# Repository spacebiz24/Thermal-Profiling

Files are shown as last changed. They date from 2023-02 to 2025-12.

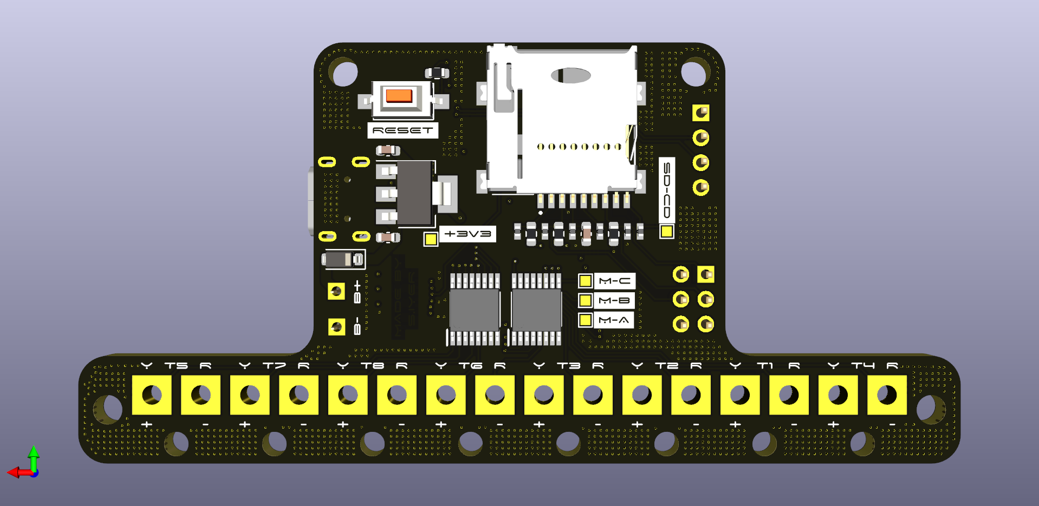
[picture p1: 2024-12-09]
Hardware/Plots/Temperature Thing With Thermocouple 3V3 Bottom.png

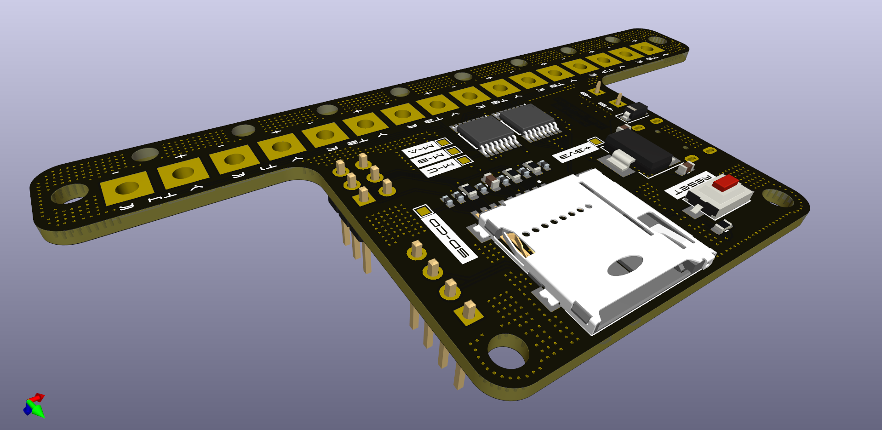
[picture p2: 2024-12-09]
Hardware/Plots/Temperature Thing With Thermocouple 3V3 Bottom Perspective.png

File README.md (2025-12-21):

# Thermal Profiling on Fabrics

This repository is divided into the following sections:

```mermaid
graph TD;
Repo --> Dashboard
Repo --> Documentation
Repo --> Firmware
Repo --> Hardware
Repo --> Thermoscope
```

Each section explains more about itself in its own `README.md` file. Please look into them.
___
Made with :heart: by [spacebiz24](https://github.com/spacebiz24), [dkoppad3](https://github.com/dkoppad3), [DivakarGC](https://github.com/DivakarGC), [naruto4526](https://github.com/naruto4526), [Eloquencere](https://github.com/Eloquencere), [Tejas-M-Nayak](https://github.com/Tejas-M-Nayak) and [L-o-n-e-W-o-l-f](https://github.com/L-o-n-e-W-o-l-f)

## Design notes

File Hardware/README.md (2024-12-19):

# Hardware
This directory contains all the files concerning the project hardware, including the PCB and the overall casing.

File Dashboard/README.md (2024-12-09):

# Dashboard
This directory contains all the files that were used to build the dashboard to display data.
Two versions were built, one implemented on a PC and the other implemented on a Raspberry Pi GUI unit.
More information can be found by looking into the sub-directories.
___
> [!WARNING]
> This version is deprecated. The final version used is found in `/Thermoscope`.

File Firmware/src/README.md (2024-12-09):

# Temperature Thing Firmware
<p align="center">
    <i align="center">The firmware running the temperature sensing platform built for DRDO. 🌡️ </i>
</p>
<p align="center">
    
    
    <br>
    
    
</p>

___

## Contents
1. [Architecture of the Firmware](#architecture-of-the-firmware)
1. [Some important pointers about the firmware](#some-important-pointers-about-the-firmware)
1. [Functions in the Firmware](#functions-in-the-firmware)
1. [Continuous Integration Pipeline](#continuous-integration-pipeline)
1. [Authors and Reviewers](#authors-and-reviewers)
1. [License](#license)

## Architecture of the Firmware
This firmware was written to interface the ATMega328P with MAX31856 ADC.
All the underlying code is written in C++ and is built using the PlatformIO framework.
The main code loop heavily relies upon the custom built MAX31856 library which is 
covered in detail in the
[library documentation](https://github.com/spacebiz24/Thermal-Profiling/tree/main/Firmware/lib/MAX31856/).

The actions performed by this firmware are:
- Choose a specific thermocouple using the MUX
- Read the temperature from the MAX31856
- Write the temperature to the serial port and SD card in CSV format
- Repeat the process all over again

The following flow chart describes the overall working of the firmware.
```mermaid
graph TD;
A[Initialise the ATMega328P Pins] --> B[Remove the existing 'data.txt' file from the SD card];
B --> C[Disable the SD card];
C --> D[Enable the MAX31856];
D --> E[Cycle through all the thermocouples and store data];
E --> F[Disable the MAX31856];
F --> G[Enable the SD card];
G --> H[Write the data to the SD card];
H --> C;
```

## Some important pointers about the firmware
All board pins are defined in the beginning of the firmware and must not be changed
as long as hardware does not change. The `SWITCHING_DELAY_MS` defines the delay between
every thermocouple and is set to ensure appropriate time for the ADC readings to be stored
without any mix up.

### Functions in the Firmware
- `selectPin(int Pin_Number)`
    - This function is used to select a specific pin using the MUX.
    - Parameters:
        - `Pin_Number`: The pin number to be selected on the MUX.
    - Returns:
        - None
- `readSingleThermocouple(int Thermocouple_Number)`
    - This function is used to read the temperature from a single thermocouple.
    It selects a thermocouple by invoking the `selectPin()` function and then reads
    the temperature from the MAX31856.
    - Parameters:
        - None
    - Returns:
        - None
- `cycleThroughThermocouples()`
    - This function is used to cycle through all the thermocouples and store the data.
    - Parameters:
        - None
    - Returns:
        - None

The `setup()` function in the firmware initialises all the pins and their directions by using the
`BOARD_PINS` and `MUX_PINS` arrays which are defined in the beginning of the firmware.
The `BOARD_PINS_DIR` array defines the direction of the pins in the `BOARD_PINS` array.
The same is not needed for `MUX_PINS` as all the pins are set as `OUTPUT`.

The `setup()` function also removes the existing data file from the SD card to ensure that new data
is always written every time. It also initialises serial communication.

The `loop()` function follows all the steps as described in the flow chart above and calls the
`cycleThroughThermocouples()` function to cycle through all the thermocouples before writing
the same data to the SD card along with the time stamp to allow easier logging.

## Continuous Integration Pipeline
The firmware is built using the PlatformIO framework and is tested using the GitHub Actions CI pipeline.
The pipeline is triggered on every push to the repository and runs the firmware on a virtual environment
and the same is configured using the `.github/workflows/main.yml` file.

## Authors
<p align="center">
<center>
<div style="display: flex; justify-content: center;" align="center">
<figure>
    <a href="https://github.com/spacebiz24">
        spacebiz24
    </a>
</figure>
</div>
</center>
</p>

## Reviewers
<p align="center">
<center>
<div style="display: flex; justify-content: center;" align="center">
<figure>
    <a href="https://github.com/Eloquencere">
        Eloquencere
    </a>
</figure>
<figure>
    <a href="https://github.com/Tejas-M-Nayak">
        Tejas-M-Nayak
    </a>
</figure>
</div>
</center>
</p>

## License
As most of the project except the SD card library is custom developed,
without prior written permission of the author, this code must not be
reproduced, displayed, modified or distributed. The SD card library is
not covered under the above license. For more information, please refer
to the LICENSE file in the root directory of the repository.

___

Made with :heart: by [spacebiz24](https://github.com/spacebiz24)

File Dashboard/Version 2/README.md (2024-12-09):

# Version 2 of the Dashboard

> [!WARNING]
> This version is deprecated. The final version used is found in `/Thermoscope`.

## SDA Troubleshooting Device

Sensor Data Analysis and Troubleshooting Device

## GUI component for troubleshooting purposes 

- Automatically mounts any drive (storage - USB, MMC)
- Copies data from the mounted drive and reboots
- Automatically runs the GUI on startup

## Setup:

1. Edit autorun to run UIV20.py on startup
2. Edit rc.local to run copy_meow.py in background
3. Reboot pi and have fun :)

### Note: Please do clone the repository and then install the dependencies.

```
git clone https://github.com/spacebiz24/Thermal-Profiling.git

pip install -r requirements.txt
```
___
Made with :heart: by [DivakarGC](https://github.com/DivakarGC)

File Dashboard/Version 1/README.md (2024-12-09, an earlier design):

# Version 1 of the Dashboard
This is version 1 of the dashboard, implemented on a PC that reads files from an SD card and displays data.

> [!WARNING]
> This version is deprecated. The final version used is found in `/Thermoscope`.

___
## Helpful Links

### Tkinter
[Use a Drag & Drop Editor to Make Tkinter Python GUI Applications!](https://www.youtube.com/watch?v=oLxFqpUbaAE)

[TkinterDesigner Documentation](https://github.com/ParthJadhav/Tkinter-Designer/blob/master/docs/instructions.md)

[Make Modern Python Dashboards With Tkinter & Matplotlib!](https://www.youtube.com/watch?v=0H19QzbBqC4)

[How to create multiple Screens/Frames using tkinter python. Tkinter Multiple Frames](https://www.youtube.com/watch?v=3yeRcxkth0I)

[Tkinter Application to Switch Between Different Page Frames](https://www.geeksforgeeks.org/tkinter-application-to-switch-between-different-page-frames/)

[How To Animate Widgets - Python Tkinter GUI Tutorial](https://www.youtube.com/watch?v=kvd6i1mXec8)

#### Tkinter Add-ons

[The ultimate introduction to modern GUIs in Python w/ tkinter](https://www.youtube.com/watch?v=mop6g-c5HEY)

[Make Tkinter Look 10x Better in 5 Minutes (CustomTkinter)](https://www.youtube.com/watch?v=Miydkti_QVE)

[CustomTkinter](https://github.com/TomSchimansky/CustomTkinter)

[tksheet](https://github.com/ragardner/tksheet)

[Python Tkinter GUI Design Using ttkbootstrap - Complete Course](https://www.youtube.com/watch?v=0tM-l_ZsxjU)

[ttkbootstrap](https://ttkbootstrap.readthedocs.io/en/latest/)

### GUI on Startup
[Convert GUI App to Real Program - Python to exe to setup wizard](https://www.youtube.com/watch?v=p3tSLatmGvU)

[The 8 Best Lightweight Operating Systems for Raspberry Pi](https://www.makeuseof.com/tag/lightweight-operating-systems-raspberry-pi/)

[Simple OS to run Tkinter Program](https://forums.raspberrypi.com/viewtopic.php?t=284516)

[Launch a GUI Tkinter program on boot](https://raspberrypi.stackexchange.com/questions/98944/launch-a-gui-tkinter-program-on-boot)

[How to get Python tkinter application to run automatically](https://stackoverflow.com/questions/76020133/how-to-get-python-tkinter-application-to-run-automatically-and-reliably-at-rpi)

___
Made with :heart: by [Eloquencere](https://github.com/Eloquencere) and [L-o-n-e-W-o-l-f](https://github.com/L-o-n-e-W-o-l-f)

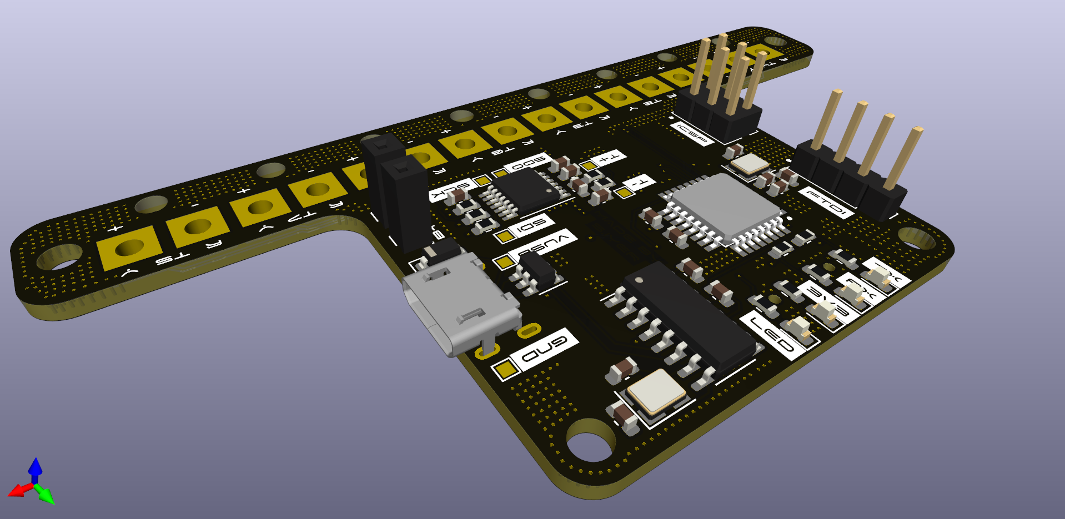
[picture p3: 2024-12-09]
Hardware/Plots/Temperature Thing With Thermocouple 3V3 Top Perspective.png

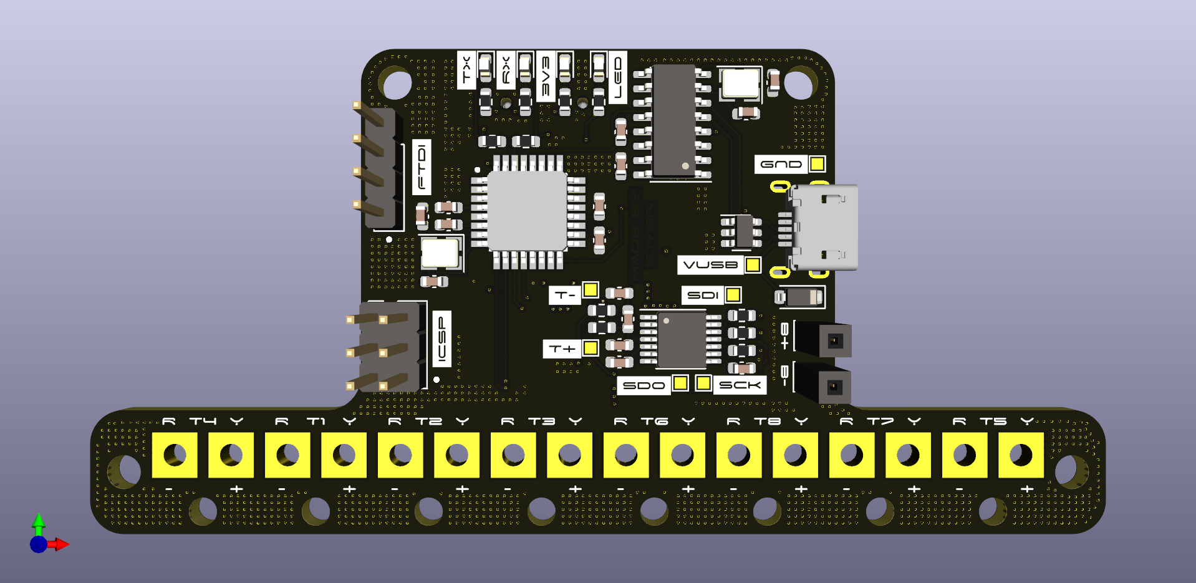
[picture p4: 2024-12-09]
Hardware/Plots/Temperature Thing With Thermocouple 3V3 Top.png

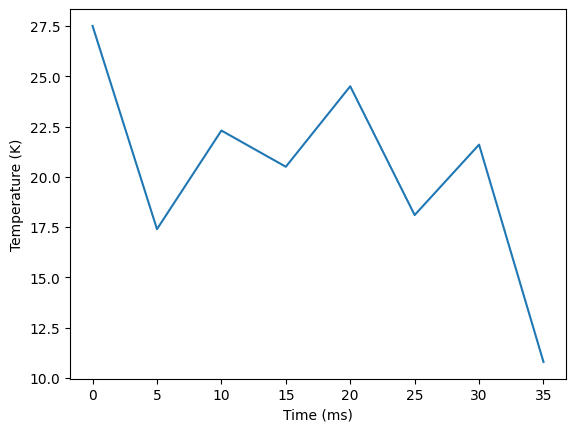
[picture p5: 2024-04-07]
Dashboard/Version 2/assets/Images/fig1.png

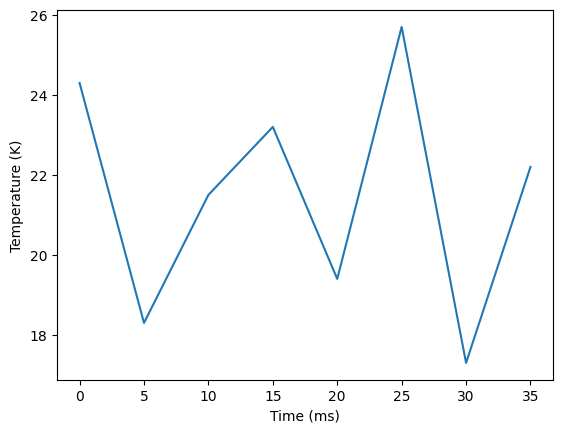
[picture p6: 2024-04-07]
Dashboard/Version 2/assets/Images/fig6.png

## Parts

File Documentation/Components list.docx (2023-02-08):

Sensors

Name | | Temperature Range | Accuracy
Thermocouple | K-Type – RdF Corporations | -184°C to +700°C | 2.2°C or 0.75%
| T-Type – Thermo Sensors | -50° to 200°C | 0.5°C or 0.75%
RTD Temperature sensor | HoneyWell | -55 °C to 150°C | ±0.5°C or ±0.2%
| Auxitrol Weston | -55°C to +322°C | ± 0.50°C
Thermistor | Semitec - 502NT-4-R025H395 | -50°C to 300°C | 1%
| Amphenol - DC95G503VN | -80°C to 150°C | ±0.1°C

Microcontroller

Name | Temperature range | Operating Voltage | ADC
Freescale Semiconductor - MPC5554 – 32-bit | –40° C to 125° C | 1.5 V ± 10% | 12-bit
Maxim Integrated MAXQ7670A – 16-bit | -40°C to +125°C | 2.5V | 12-bit
Vorago Technologies VA41620 – 32-bit | -55 to 125℃ | 3.3 +/- 0.33V | 12-bit
Atmel SAM3X8E – 32-bit | -55°C to 105°C | 1.62V | 12-bit
Microchip ATmegaS64M1 – 8-bit | -55 °C to +125 °C | 3.3V | 10-bit

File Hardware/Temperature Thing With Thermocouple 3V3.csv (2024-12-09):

Source: | C:\Users\Desktop\Documents\KiCad\Temperature Thing With Thermocouple 3V3\Temperature Thing With Thermocouple 3V3.kicad_sch
Date: | 08-07-2024 10:46:44
Tool: | Eeschema (7.0.0)
Generator: | C:\Program Files\KiCad\7.0\bin\scripting\plugins/bom_csv_grouped_by_value.py
Component Count: | 86
Collated Components:
Item | Qty | Reference(s) | Value | LibPart | Footprint | Datasheet | DNP | Height | MANUFACTURER | Manufacturer_Name | Manufacturer_Part_Number | Mouser Part Number | Mouser Price/Stock | Sim.Device | Sim.Pins
1 | 6 | C1, C2, C3, C5, C7, C13 | 100n | Device:C | Capacitor_SMD:C_0603_1608Metric | ~
2 | 2 | C4, C8 | 10n | Device:C | Capacitor_SMD:C_0603_1608Metric | ~
3 | 4 | C6, C9, C15, C16 | 22p | Device:C | Capacitor_SMD:C_0603_1608Metric | ~
4 | 2 | C10, C12 | 1u | Device:C | Capacitor_SMD:C_0603_1608Metric | ~
5 | 1 | C11 | 4.7u | Device:C | Capacitor_SMD:C_0603_1608Metric | ~
6 | 1 | C14 | 10u | Device:C | Capacitor_SMD:C_0603_1608Metric | ~
7 | 2 | C17, C18 | 10u | Device:C_Polarized_US | Capacitor_SMD:C_0603_1608Metric | ~
8 | 4 | D1, D2, D3, D4 | LED | Device:LED | LED_SMD:LED_0603_1608Metric | ~
9 | 2 | D5, D6 | 1N4148 | Diode:1N4148 | Diode_SMD:D_SOD-123 | https://assets.nexperia.com/documents/data-sheet/1N4148_1N4448.pdf |  |  |  |  |  |  |  |  | D | 1=K 2=A
10 | 1 | J1 | T1+ | Connector:Conn_01x01_Pin | Connector_PinHeader_1.27mm:PinHeader_1x01_P1.27mm_Vertical | ~
11 | 1 | J2 | T2+ | Connector:Conn_01x01_Pin | Connector_PinHeader_1.27mm:PinHeader_1x01_P1.27mm_Vertical | ~
12 | 1 | J3 | T3+ | Connector:Conn_01x01_Pin | Connector_PinHeader_1.27mm:PinHeader_1x01_P1.27mm_Vertical | ~
13 | 1 | J4 | T4+ | Connector:Conn_01x01_Pin | Connector_PinHeader_1.27mm:PinHeader_1x01_P1.27mm_Vertical | ~
14 | 1 | J5 | T5+ | Connector:Conn_01x01_Pin | Connector_PinHeader_1.27mm:PinHeader_1x01_P1.27mm_Vertical | ~
15 | 1 | J6 | T6+ | Connector:Conn_01x01_Pin | Connector_PinHeader_1.27mm:PinHeader_1x01_P1.27mm_Vertical | ~
16 | 1 | J7 | T7+ | Connector:Conn_01x01_Pin | Connector_PinHeader_1.27mm:PinHeader_1x01_P1.27mm_Vertical | ~
17 | 1 | J8 | T8+ | Connector:Conn_01x01_Pin | Connector_PinHeader_1.27mm:PinHeader_1x01_P1.27mm_Vertical | ~
18 | 1 | J9 | T1- | Connector:Conn_01x01_Pin | Connector_PinHeader_1.27mm:PinHeader_1x01_P1.27mm_Vertical | ~
19 | 1 | J10 | T2- | Connector:Conn_01x01_Pin | Connector_PinHeader_1.27mm:PinHeader_1x01_P1.27mm_Vertical | ~
20 | 1 | J11 | T3- | Connector:Conn_01x01_Pin | Connector_PinHeader_1.27mm:PinHeader_1x01_P1.27mm_Vertical | ~
21 | 1 | J12 | T4- | Connector:Conn_01x01_Pin | Connector_PinHeader_1.27mm:PinHeader_1x01_P1.27mm_Vertical | ~
22 | 1 | J13 | USB_B_Micro | Connector:USB_B_Micro | Connector_USB:USB_Micro-B_Molex_47346-0001 | ~
23 | 1 | J14 | T5- | Connector:Conn_01x01_Pin | Connector_PinHeader_1.27mm:PinHeader_1x01_P1.27mm_Vertical | ~
24 | 1 | J15 | T6- | Connector:Conn_01x01_Pin | Connector_PinHeader_1.27mm:PinHeader_1x01_P1.27mm_Vertical | ~
25 | 1 | J16 | B+ | Connector:Conn_01x01_Pin | Connector_PinSocket_2.54mm:PinSocket_1x01_P2.54mm_Vertical | ~
26 | 1 | J17 | T7- | Connector:Conn_01x01_Pin | Connector_PinHeader_1.27mm:PinHeader_1x01_P1.27mm_Vertical | ~
27 | 1 | J18 | ICSP | Connector_Generic:Conn_02x03_Odd_Even | Connector_PinHeader_2.54mm:PinHeader_2x03_P2.54mm_Vertical | ~
28 | 1 | J19 | T8- | Connector:Conn_01x01_Pin | Connector_PinHeader_1.27mm:PinHeader_1x01_P1.27mm_Vertical | ~
29 | 1 | J20 | B- | Connector:Conn_01x01_Pin | Connector_PinSocket_2.54mm:PinSocket_1x01_P2.54mm_Vertical | ~
30 | 7 | R1, R2, R3, R6, R7, R14, R15 | 1k | Device:R_US | Resistor_SMD:R_0603_1608Metric | ~
31 | 2 | R4, R5 | 100 | Device:R_US | Resistor_SMD:R_0603_1608Metric | ~
32 | 6 | R8, R9, R10, R11, R12, R13 | 10k | Device:R_US | Resistor_SMD:R_0603_1608Metric | ~
33 | 6 | RV1, RV2, RV3, RV4, RV5, RV6 | CG0402MLU-3.3G | CG402MLU-3_3G:CG0402MLU-3.3G | CG402MLU-3_3G:CG402MLU-3_3G | https://www.bourns.com/docs/Product-Datasheets/MLU.pdf |  |  | 0.41 |  | Bourns | CG0402MLU-3.3G | 652-CG0402MLU-3.3G | https://www.mouser.co.uk/ProductDetail/Bourns/CG0402MLU-3.3G?qs=m8myXnDJXpWVM8EQWErxtQ%3D%3D
34 | 1 | SW1 | SW_Push | Switch:SW_Push | Button_Switch_SMD:SW_SPST_CK_RS282G05A3 | ~
35 | 10 | TP1, TP2, TP3, TP4, TP5, TP6, TP7, TP8, TP9, TP10 | ~ | Connector:TestPoint | TestPoint:TestPoint_Pad_1.0x1.0mm | ~
36 | 1 | U1 | CH340G | Interface_USB:CH340G | Package_SO:SOIC-16_3.9x9.9mm_P1.27mm | http://www.datasheet5.com/pdf-local-2195953
37 | 1 | U2 | MAX31856 | Sensor_Temperature:MAX31856 | Package_SO:TSSOP-14_4.4x5mm_P0.65mm | https://datasheets.maximintegrated.com/en/ds/MAX31856.pdf
38 | 2 | U3, U6 | CD4051B | Analog_Switch:CD4051B | CD4051BPWR:CD4051BPWR | http://www.ti.com/lit/ds/symlink/cd4052b.pdf
39 | 1 | U4 | microSD Card | GCT-MICROSD-HOLDER:GCT-MICROSD-HOLDER | GCT-MICROSD-HOLDER:GCT-MICROSD-HOLDER
40 | 1 | U5 | ATMEGA328P-AU | ATMEGA328P-AU:ATMEGA328P-AU | ATMEGA328P-AU:ATMEGA328P-AU |  |  |  |  | Atmel
41 | 1 | U7 | USBLC6-2SC6 | Power_Protection:USBLC6-2SC6 | Package_TO_SOT_SMD:SOT-23-6 | https://www.st.com/resource/en/datasheet/usblc6-2.pdf
42 | 1 | U8 | AMS1117-3.3 | Regulator_Linear:AMS1117-3.3 | Package_TO_SOT_SMD:SOT-223-3_TabPin2 | http://www.advanced-monolithic.com/pdf/ds1117.pdf
43 | 1 | Y1 | 12MHz | Device:Crystal_GND24 | Crystal:Crystal_SMD_3225-4Pin_3.2x2.5mm | ~
44 | 1 | Y2 | 16MHz | Device:Crystal_GND24 | Crystal:Crystal_SMD_3225-4Pin_3.2x2.5mm | ~

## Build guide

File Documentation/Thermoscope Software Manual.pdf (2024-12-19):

# T H E R M O S C O P E S O F T W A R E M A N U A L

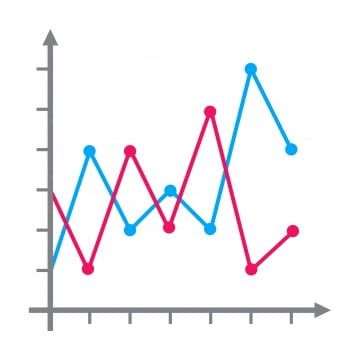
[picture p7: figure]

# A B O U T T H E A P P

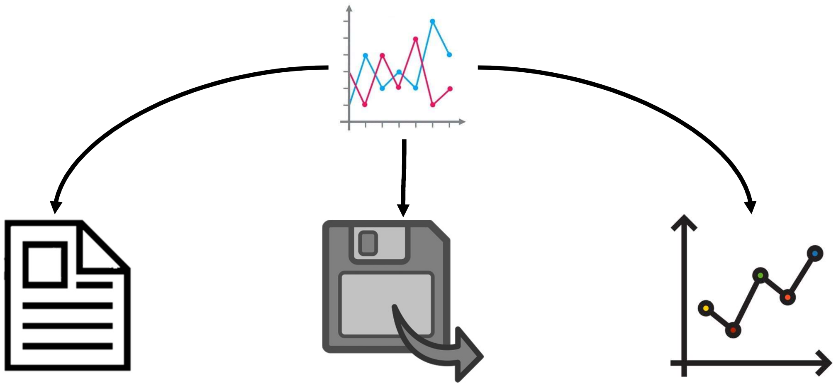
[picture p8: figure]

Read | Capture | Visualise

# I M P O R T A N T !

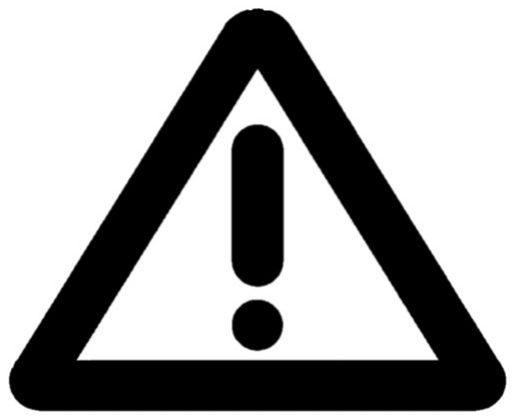
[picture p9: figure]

# Please follow the steps in the specified order for reliable

performance.

# S T E P 1 : C O N N E C T I N G T H E S D C A R D

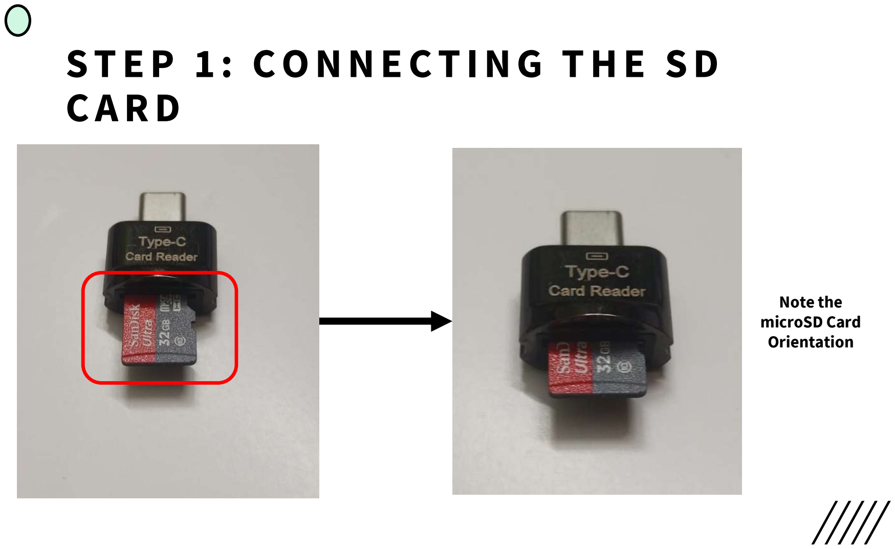
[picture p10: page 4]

Note the
microSD Card
Orientation

# S T E P 2 : C O N N E C T I N G T H E S D C A R D R E A D E R

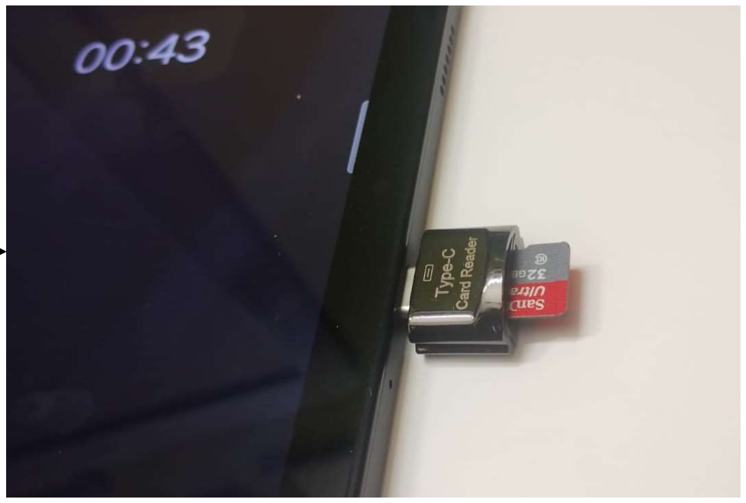
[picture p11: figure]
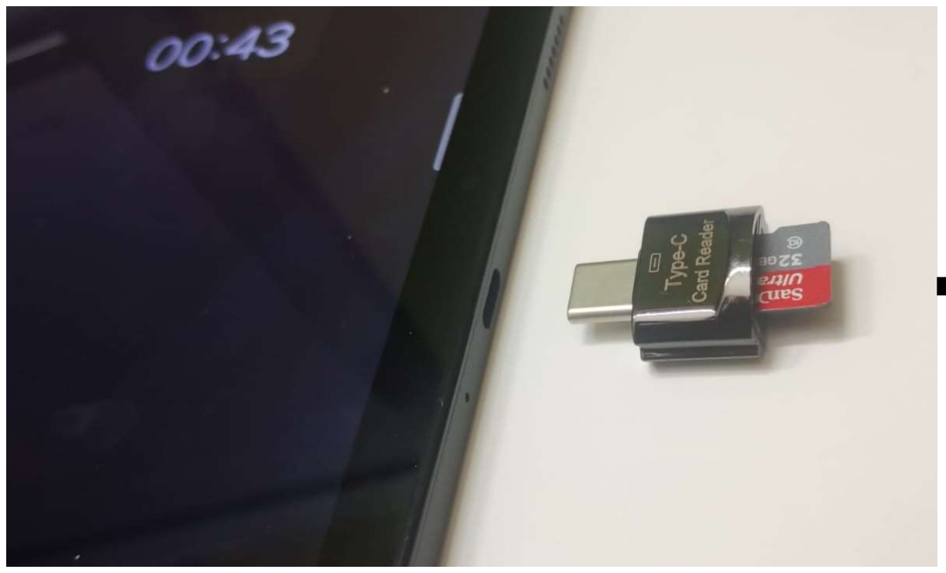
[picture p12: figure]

# S T E P 3 : O P E N I N G T H E A P P

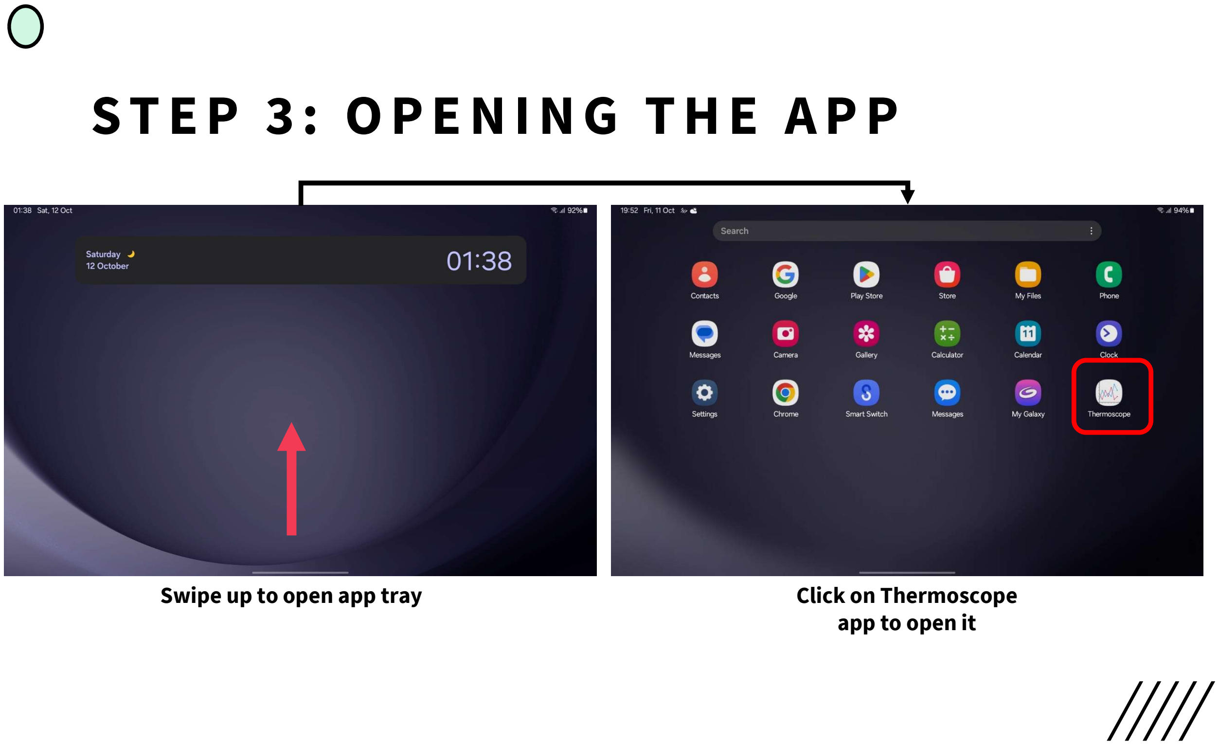
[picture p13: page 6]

Swipe up to open app tray | Click on Thermoscope app to open it

# S T E P 4 : S A V I N G T H E D A T A F I L E

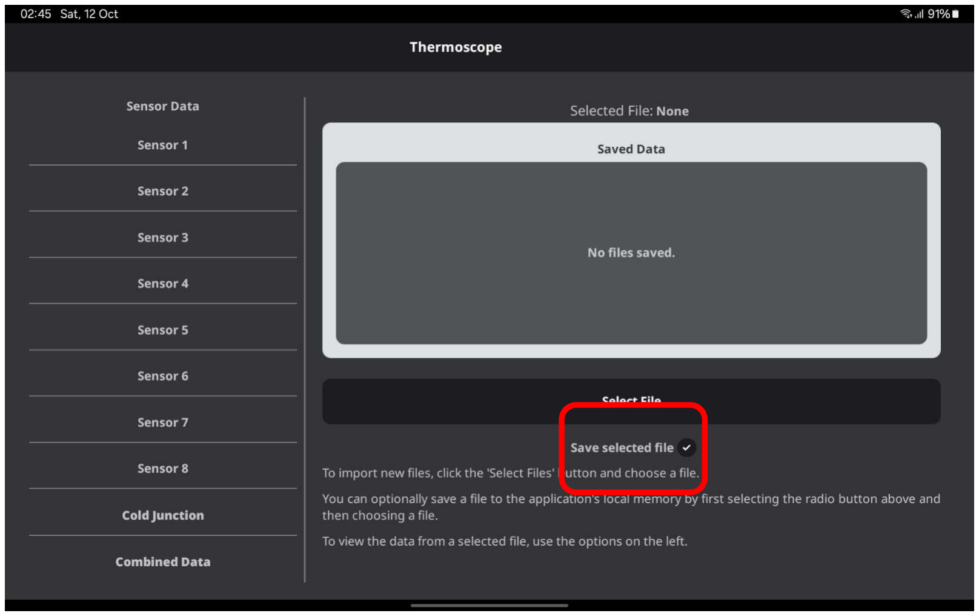
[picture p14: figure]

Optionally, if the save
file button is selected,
then the file will be
stored on the device
and will be accessible
even if the application
is closed and reopened.

# S T E P 5 A : C H O O S I N G T H E D A T A F I L E

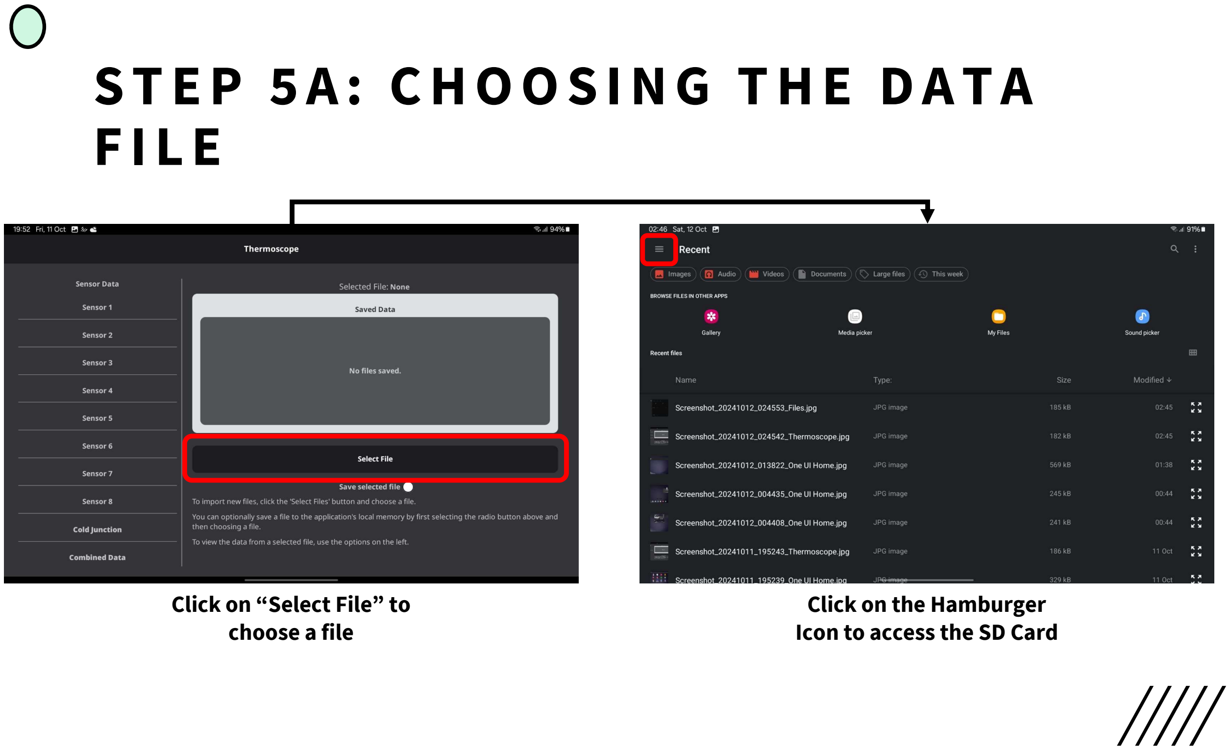
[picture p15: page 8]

Click on “Select File” to
choose a file

Click on the Hamburger
Icon to access the SD Card

# S T E P 5 B : C H O O S I N G T H E D A T A F I L E

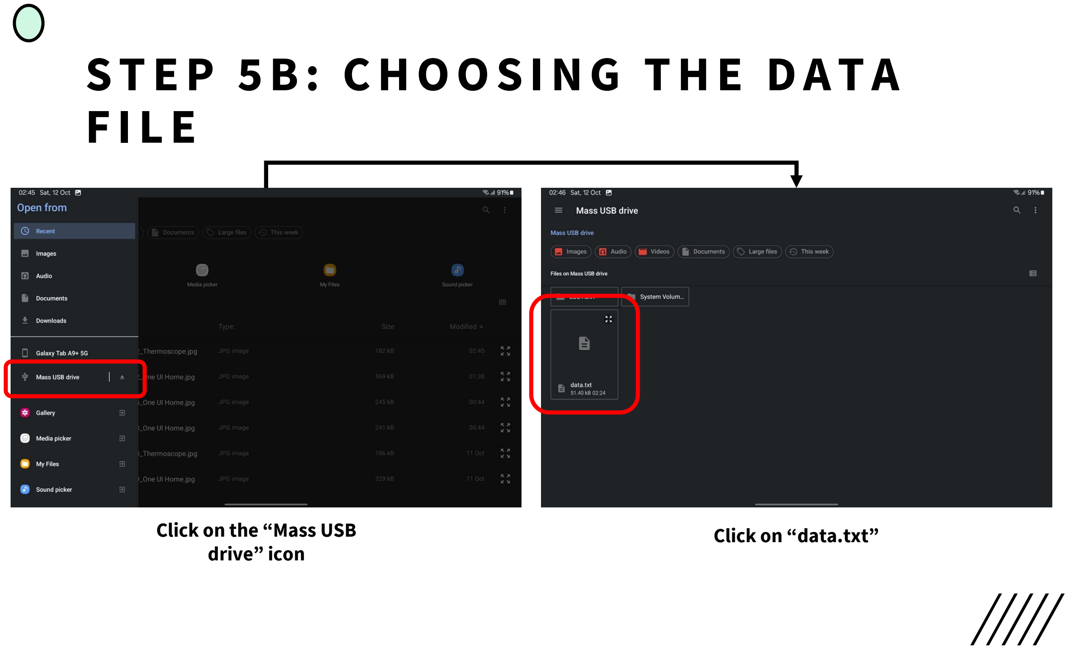
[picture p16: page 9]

Click on the “Mass USB
drive” icon

Click on “data.txt”

# S T E P 6 A : V I E W I N G T H E D A T A

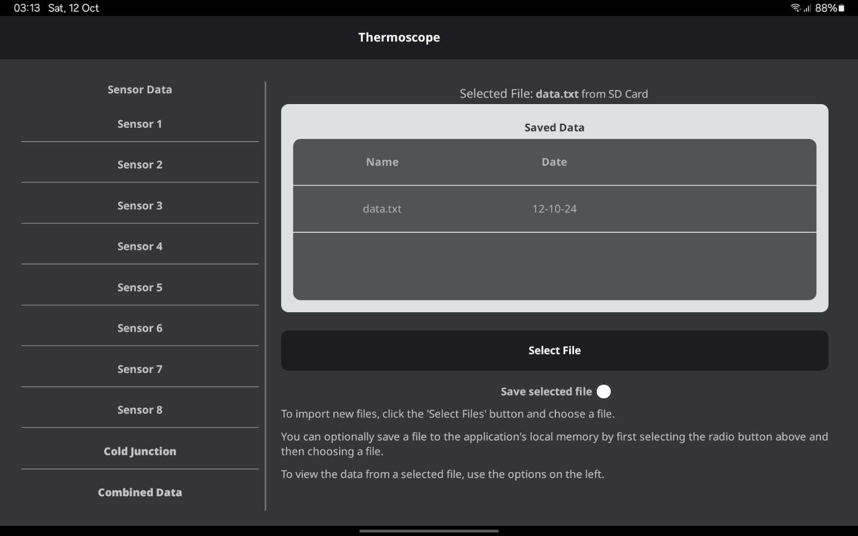
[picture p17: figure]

After successful
selection of the data
file, you should be
presented with this
window

# S T E P 6 B : V I E W I N G T H E D A T A

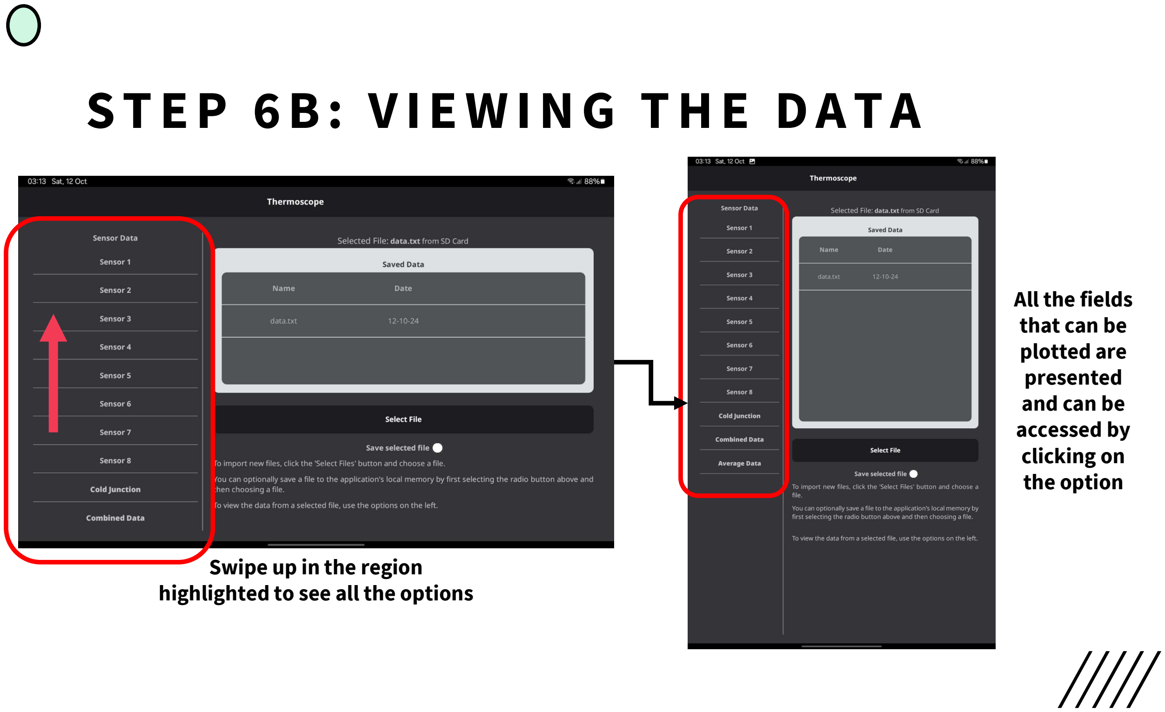
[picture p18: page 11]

Swipe up in the region
highlighted to see all the options

All the fields
that can be
plotted are
presented
and can be
accessed by
clicking on
the option

# S T E P 7 A : V E R T I C A L Z O O M F E A T U R E S W H I L E V I E W I N G D A T A

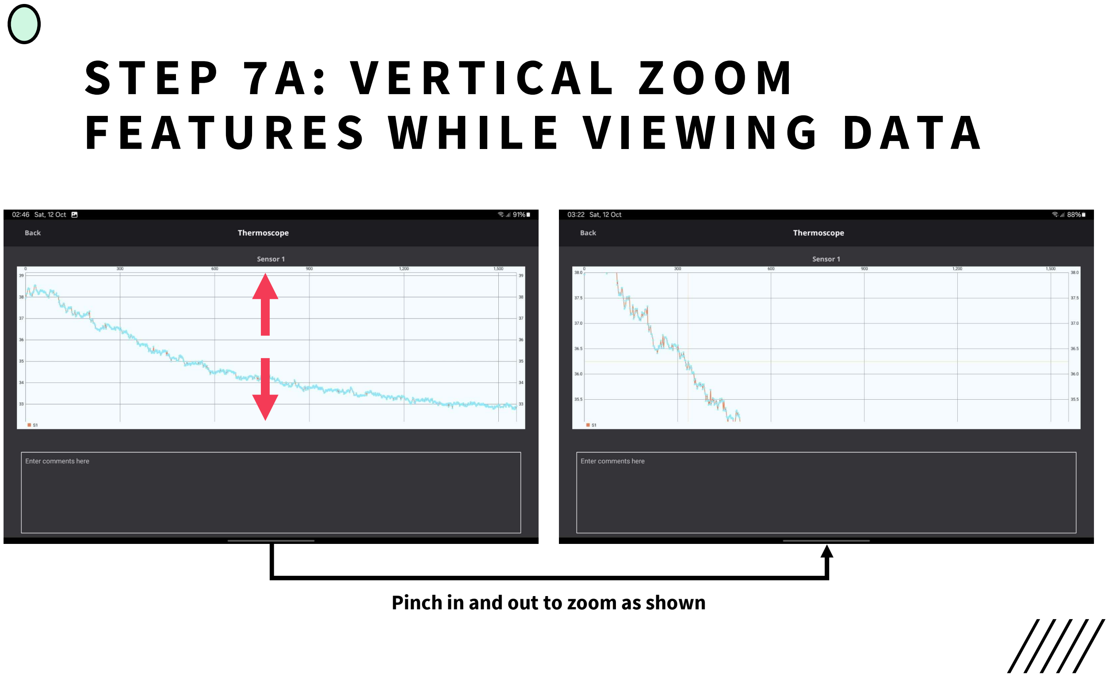
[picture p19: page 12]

Pinch in and out to zoom as shown

# S T E P 7 B : H O R I Z O N T A L Z O O M F E A T U R E S W H I L E V I E W I N G D A T A

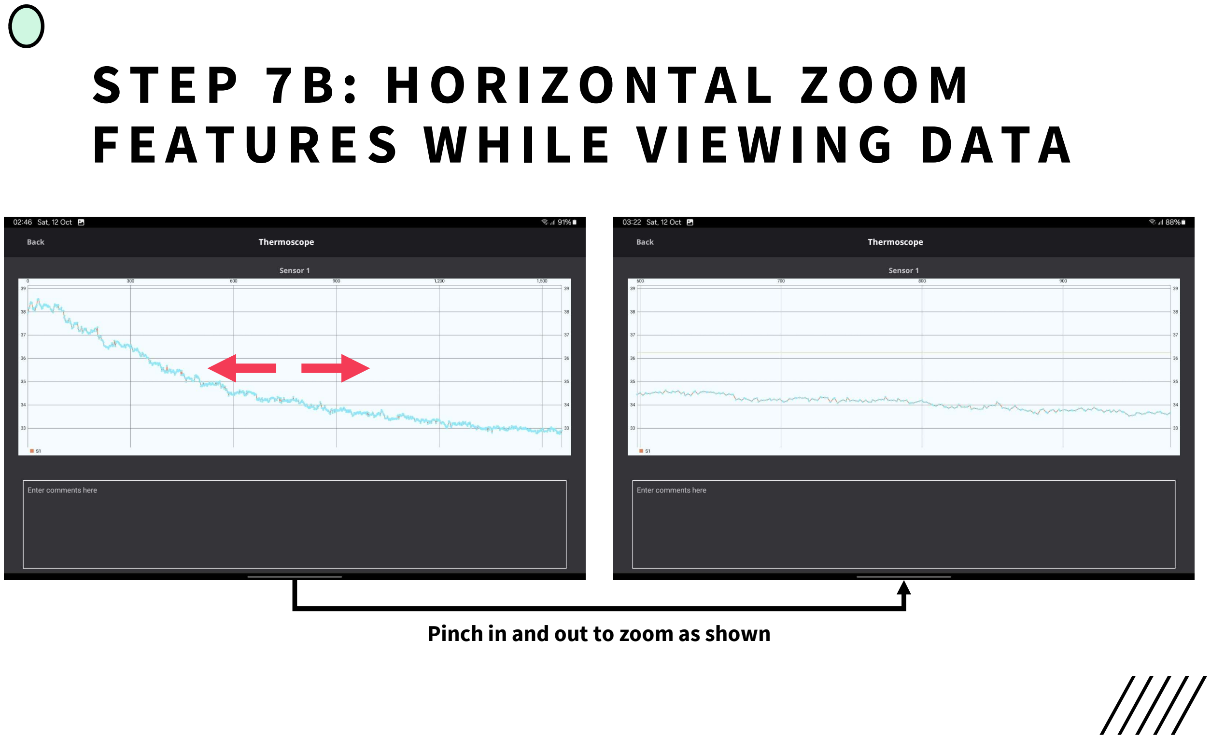
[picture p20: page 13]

Pinch in and out to zoom as shown

# S T E P 7 C : P A N N I N G F E A T U R E S W H I L E V I E W I N G D A T A

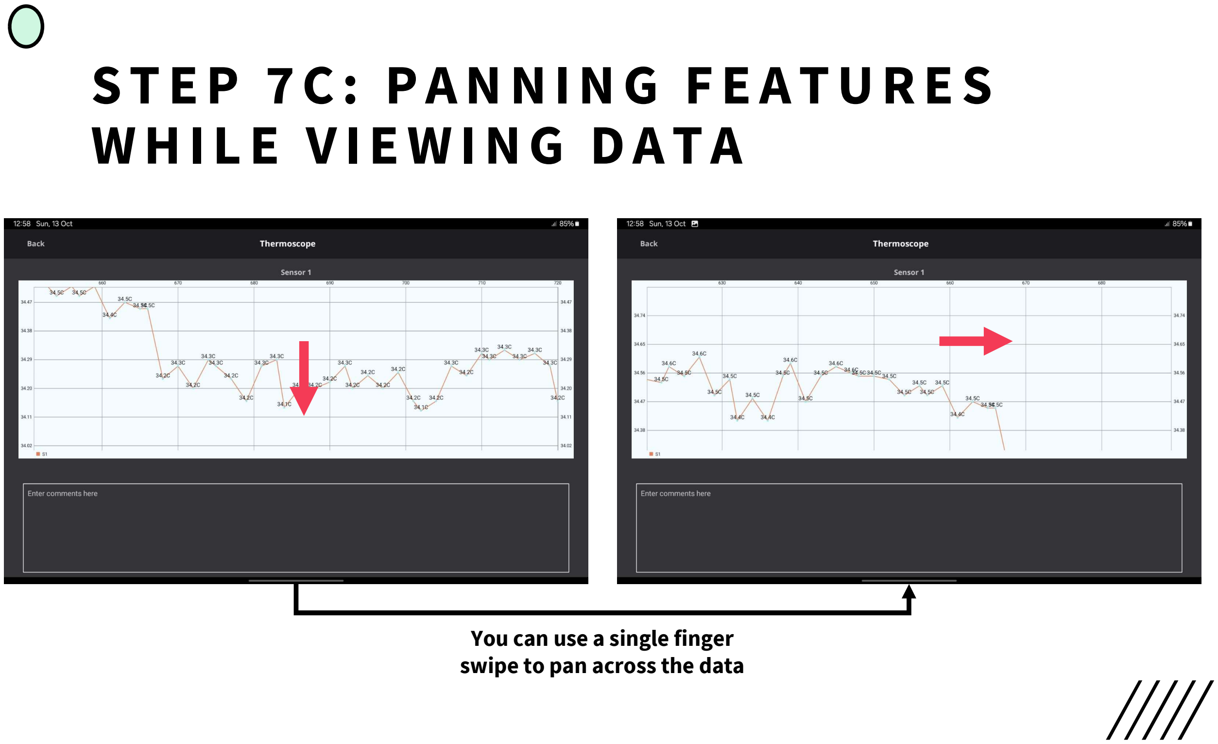
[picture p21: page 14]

You can use a single finger swipe to pan across the data

# S T E P 8 A : F E A T U R E S O F T H E V I E W I N G W I N D O W

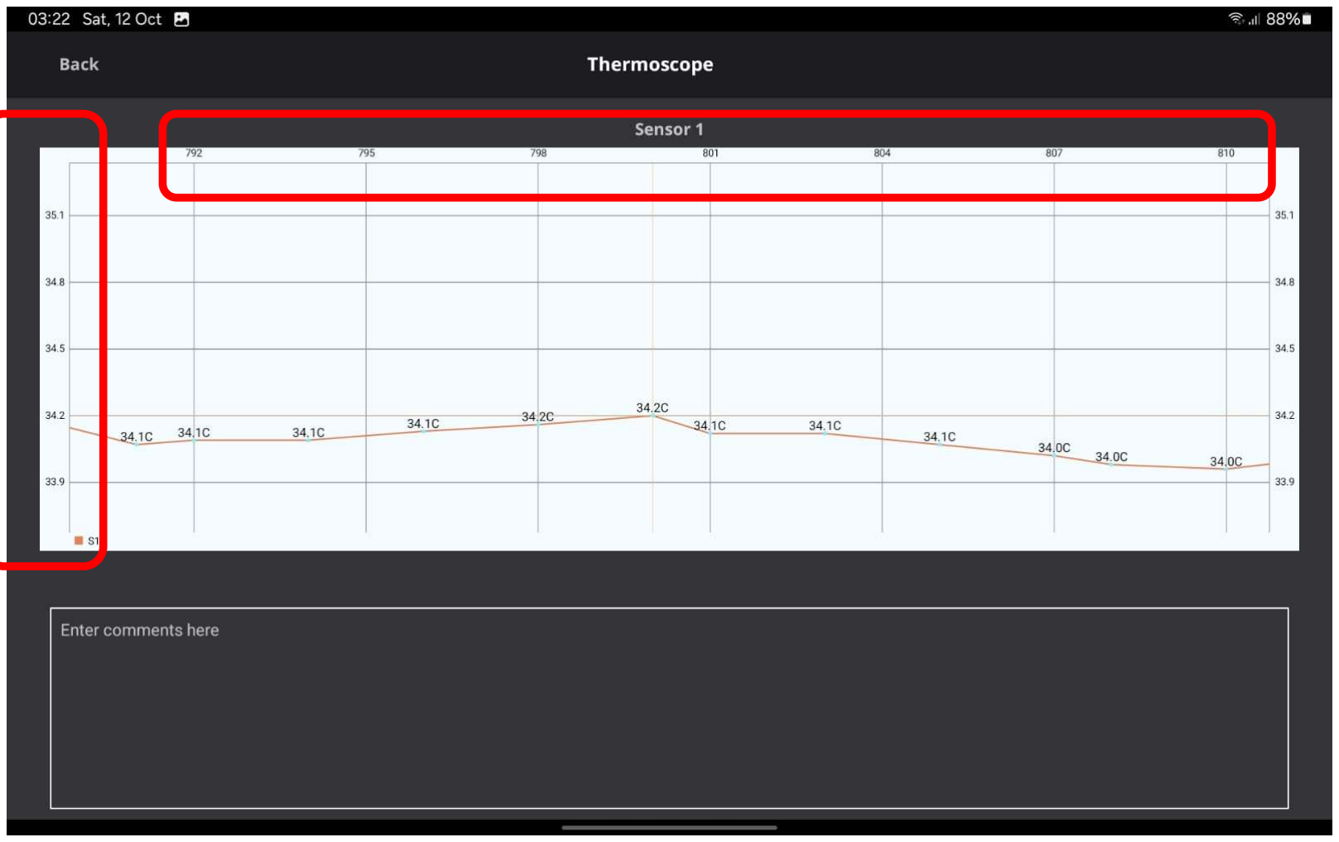
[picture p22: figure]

The Y-Axis
gives the
temperature

The X-Axis
gives the
time stamp

# S T E P 8 B : F E A T U R E S O F T H E V I E W I N G W I N D O W

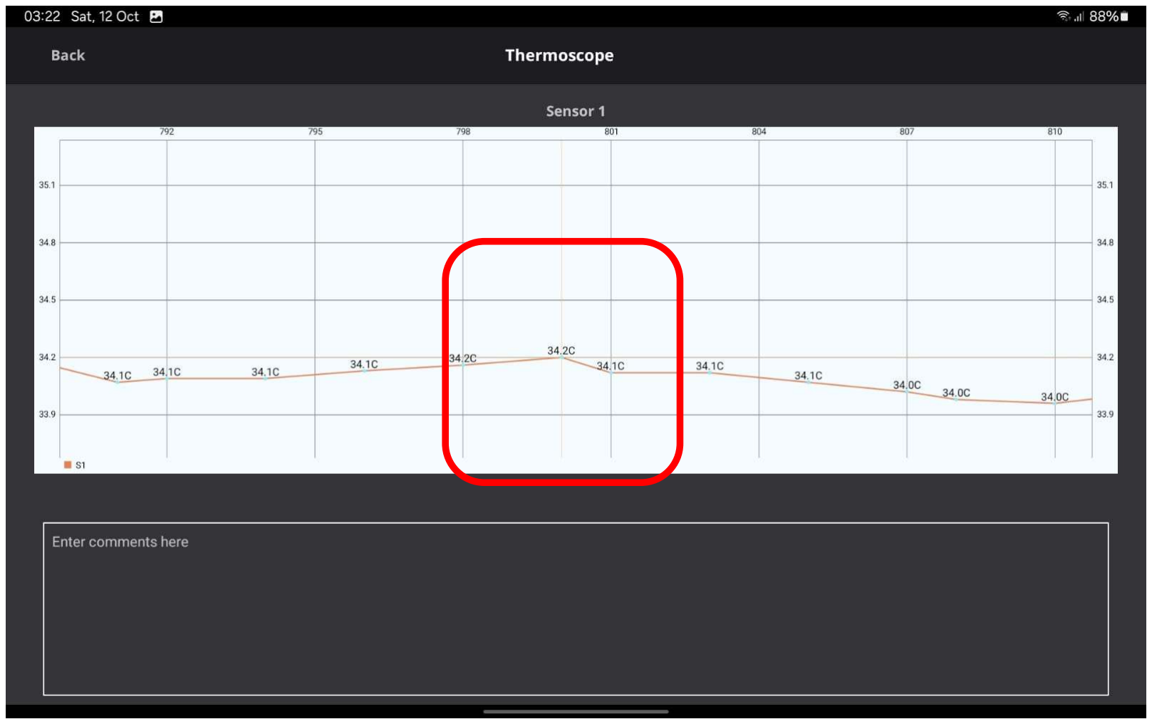
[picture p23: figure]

The Yellow lines help
to give the X and Y-Axis values and can
be viewed by
clicking on different
points

# S T E P 8 C : F E A T U R E S O F T H E V I E W I N G W I N D O W

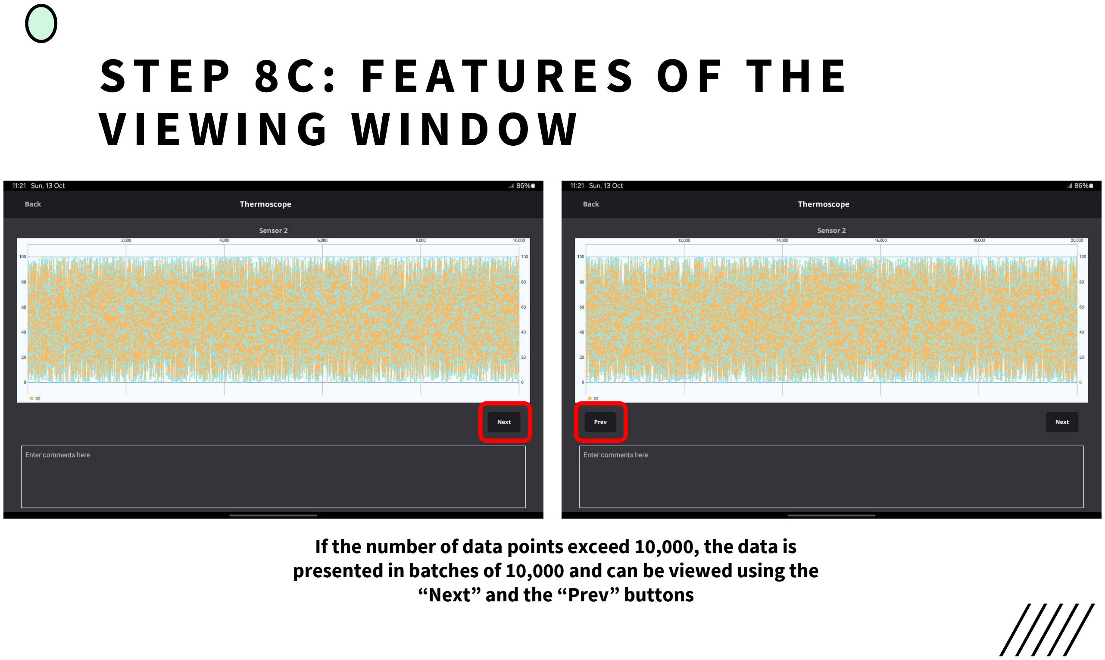
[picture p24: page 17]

If the number of data points exceed 10,000, the data is presented in batches of 10,000 and can be viewed using the “Next” and the “Prev” buttons

# S T E P 9 : E X I T I N G T H E A P P S A F E L Y

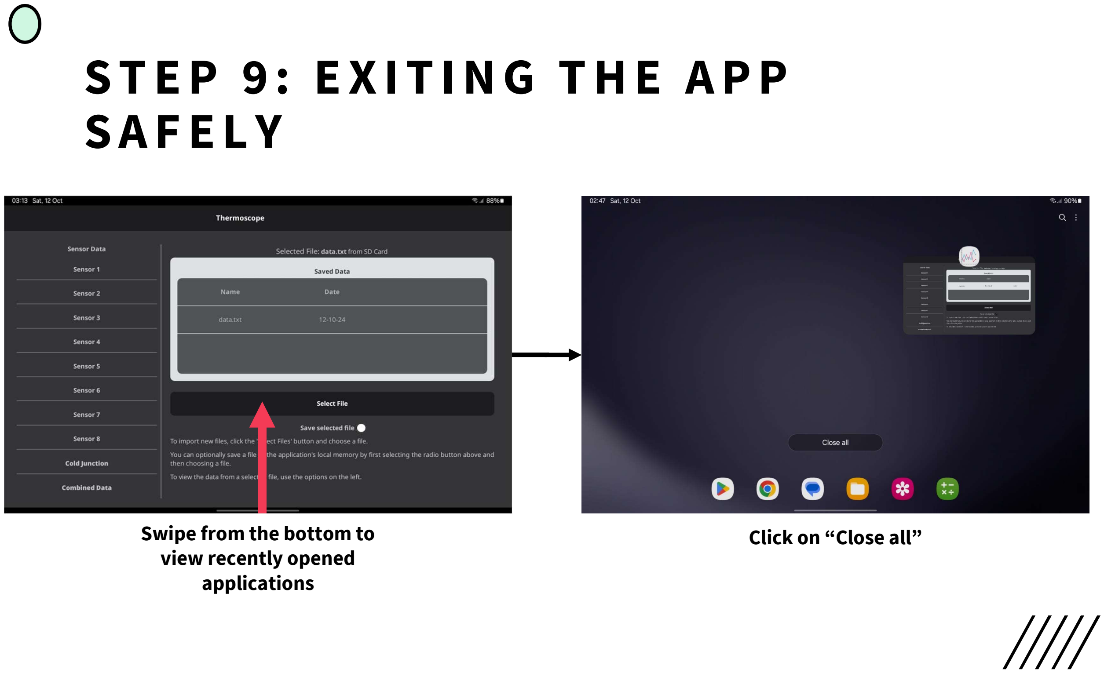
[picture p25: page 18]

Swipe from the bottom to
view recently opened
applications

Click on “Close all”

# S T E P 1 0 A : E J E C T I N G T H E S D C A R D

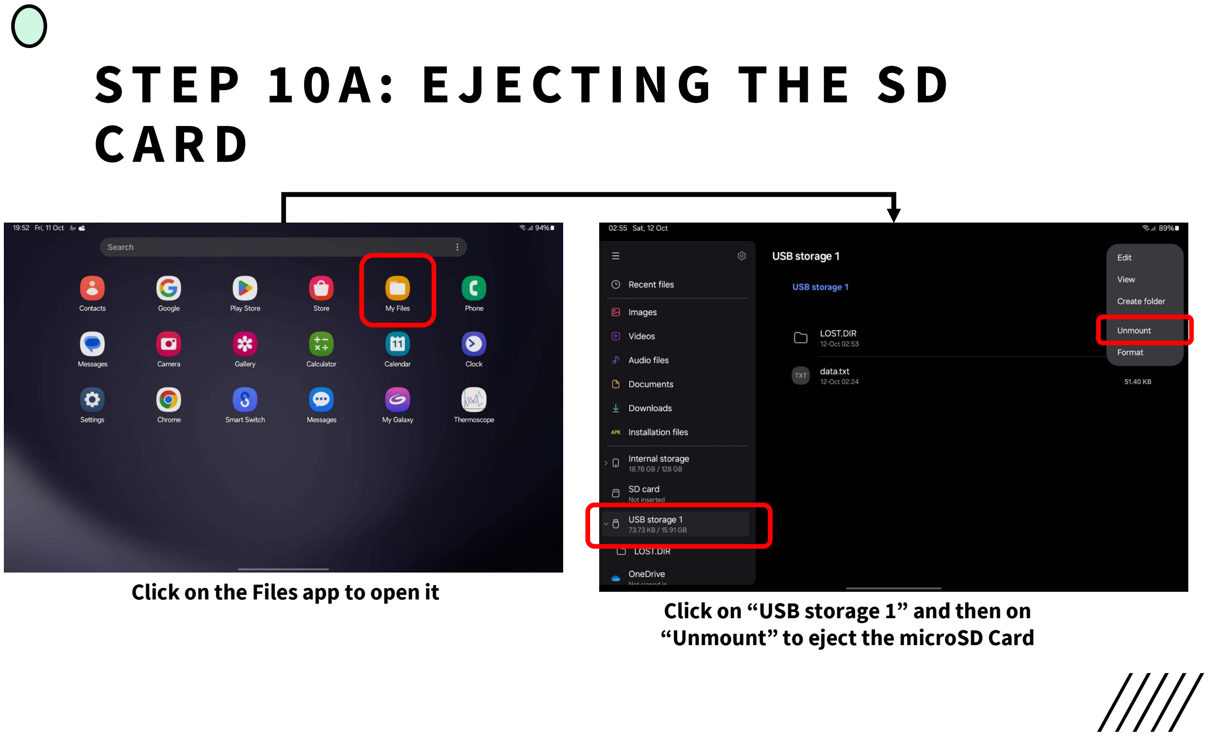
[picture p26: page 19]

Click on the Files app to open it | Click on “USB storage 1” and then on
| “Unmount” to eject the microSD Card

# S T E P 1 0 B : E J E C T I N G T H E S D C A R D

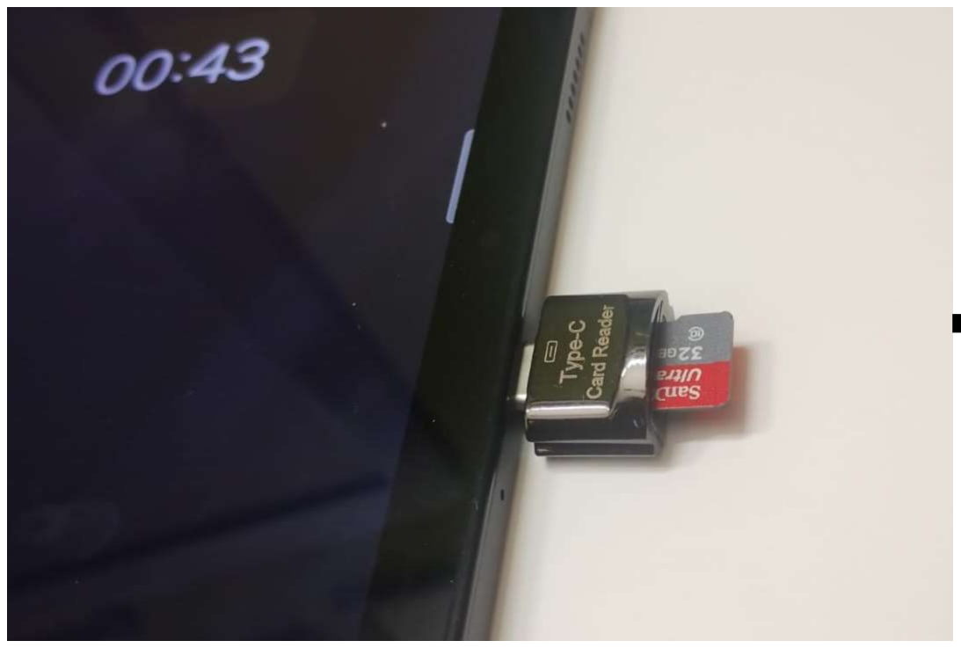
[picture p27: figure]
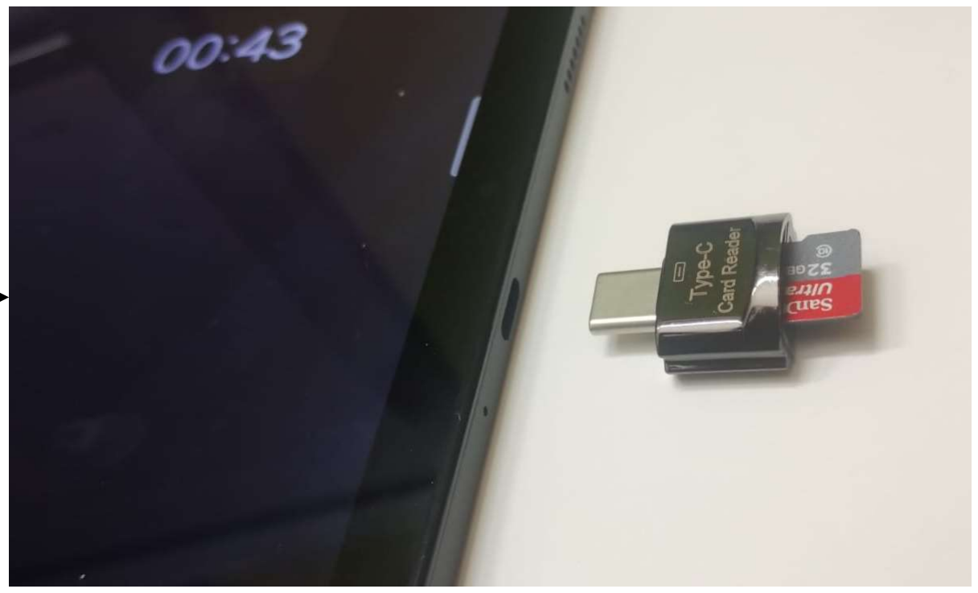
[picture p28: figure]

Made By, • Dr. Deepali Koppad • Siddhaanth S Iyer • Subasree M

- TM Srirangarajan • Tejas M Nayak • Divakar GC • Shakthi Varun • Vaishanth Bharadwaj • Bharath Bhaskar

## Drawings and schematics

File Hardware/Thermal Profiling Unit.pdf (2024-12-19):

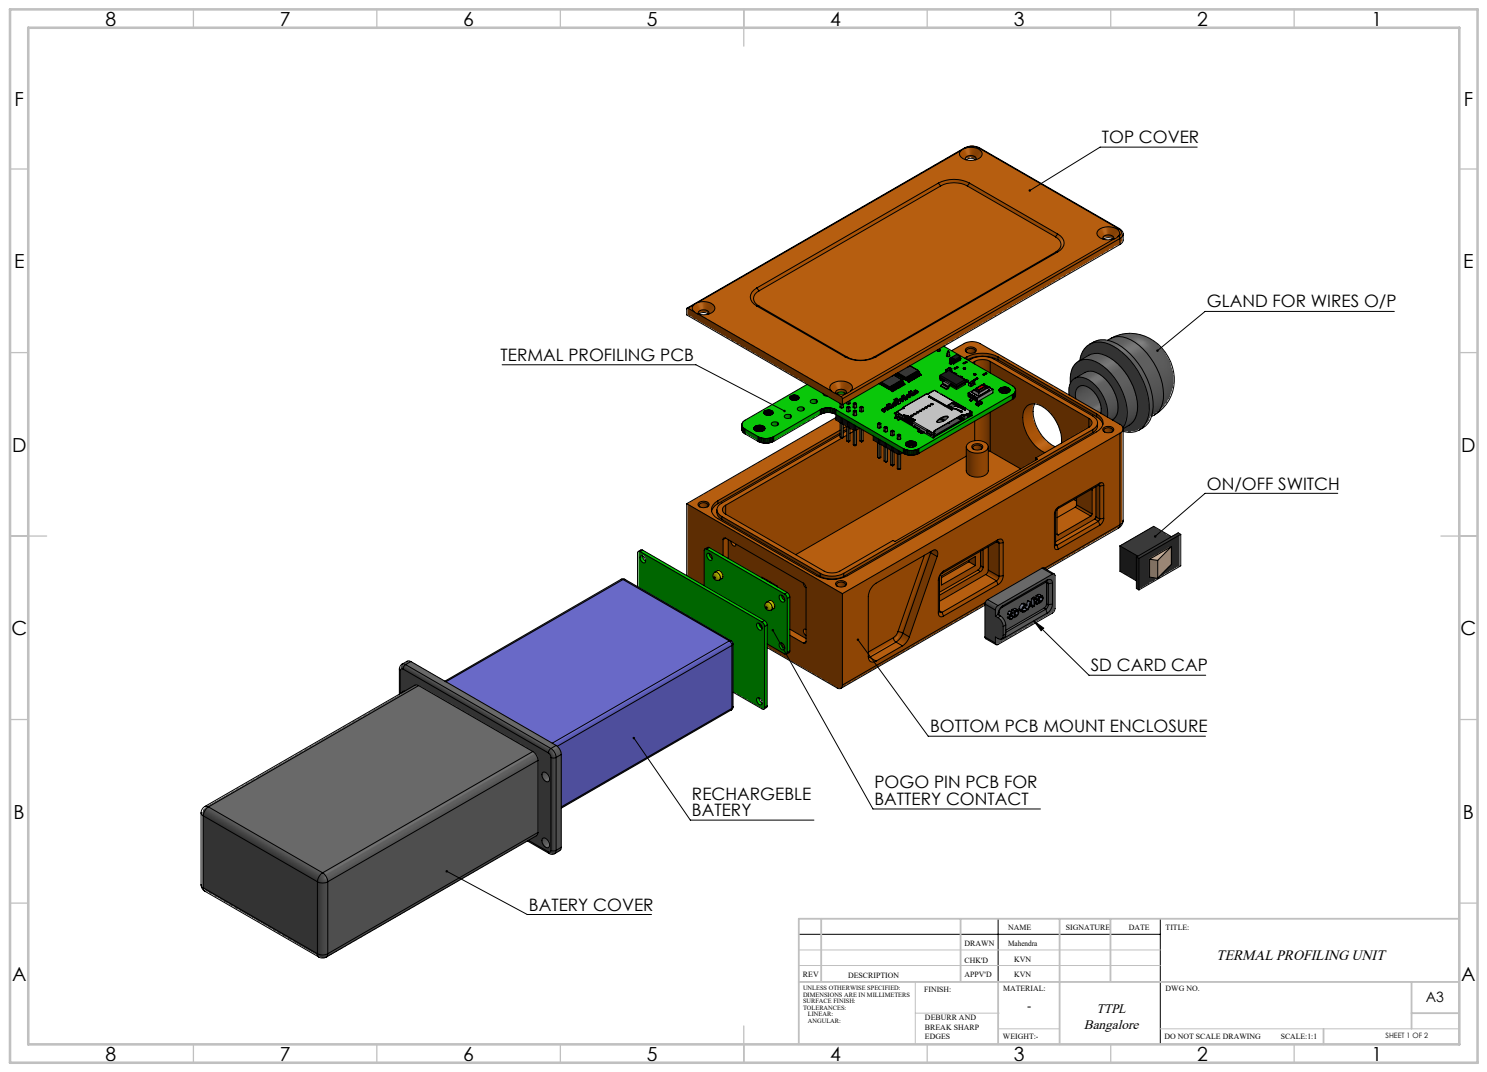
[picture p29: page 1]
TOP COVER; BATERY COVER; DEBURR AND BREAK SHARP; SCALE:1:1; SHEET 1 OF 2

GLAND FOR WIRES O/P

TERMAL PROFILING PCB

ON/OFF SWITCH

SD CARD CAP

BOTTOM PCB MOUNT ENCLOSURE

POGO PIN PCB FOR

BATTERY CONTACT RECHARGEBLE
BATERY

NAME | SIGNATURE | DATE | TITLE: TERMAL PROFILING UNIT

DRAWN | Mahendra
CHK'D | KVN

REV | DESCRIPTION | APPV'D | KVN
UNLESS OTHERWISE SPECIFIED: DIMENSIONS ARE IN MILLIMETERS SURFACE FINISH: TOLERANCES: LINEAR: ANGULAR: | FINISH: | MATERIAL: | TTPL Bangalore | DWG NO. | A3 -

DO NOT SCALE DRAWING

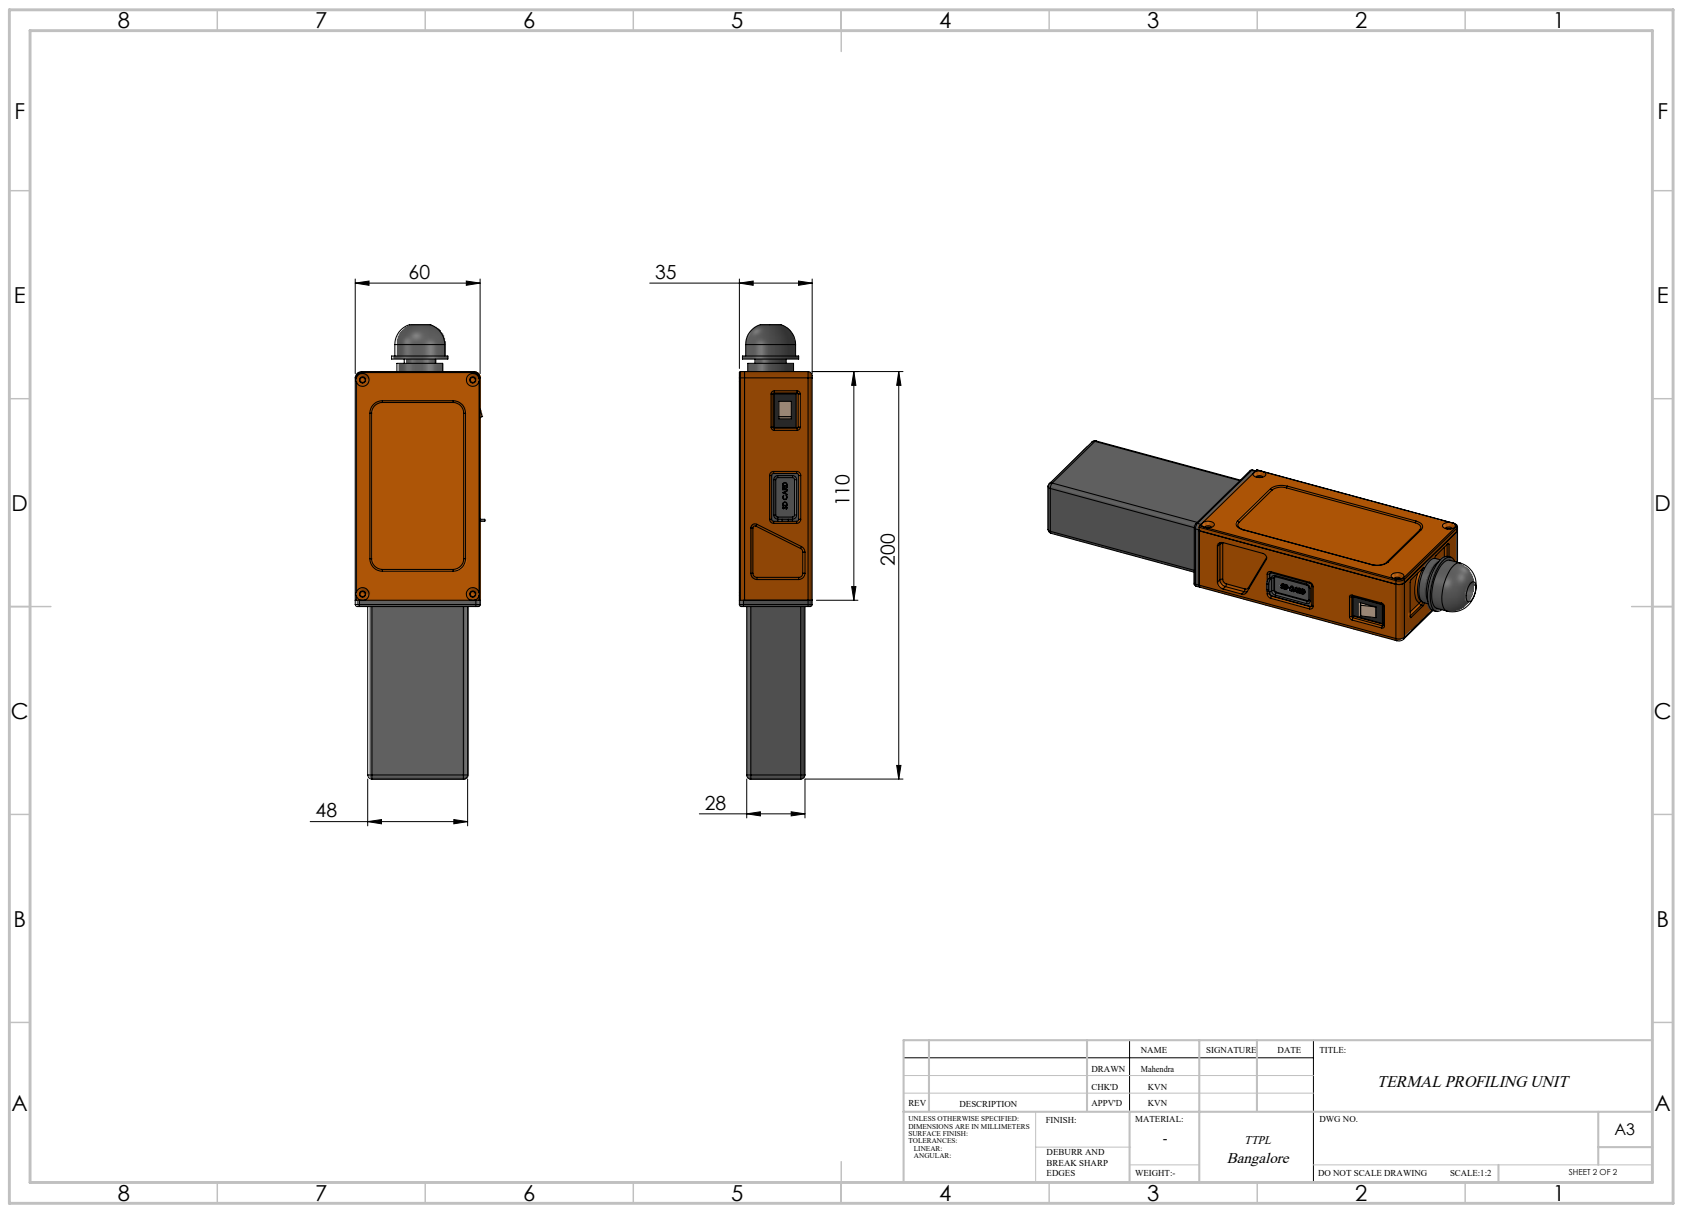
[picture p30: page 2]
DEBURR AND BREAK SHARP; SCALE:1:2; SHEET 2 OF 2

NAME | SIGNATURE | DATE | TITLE: TERMAL PROFILING UNIT

DRAWN | Mahendra
CHK'D | KVN

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

DO NOT SCALE DRAWING

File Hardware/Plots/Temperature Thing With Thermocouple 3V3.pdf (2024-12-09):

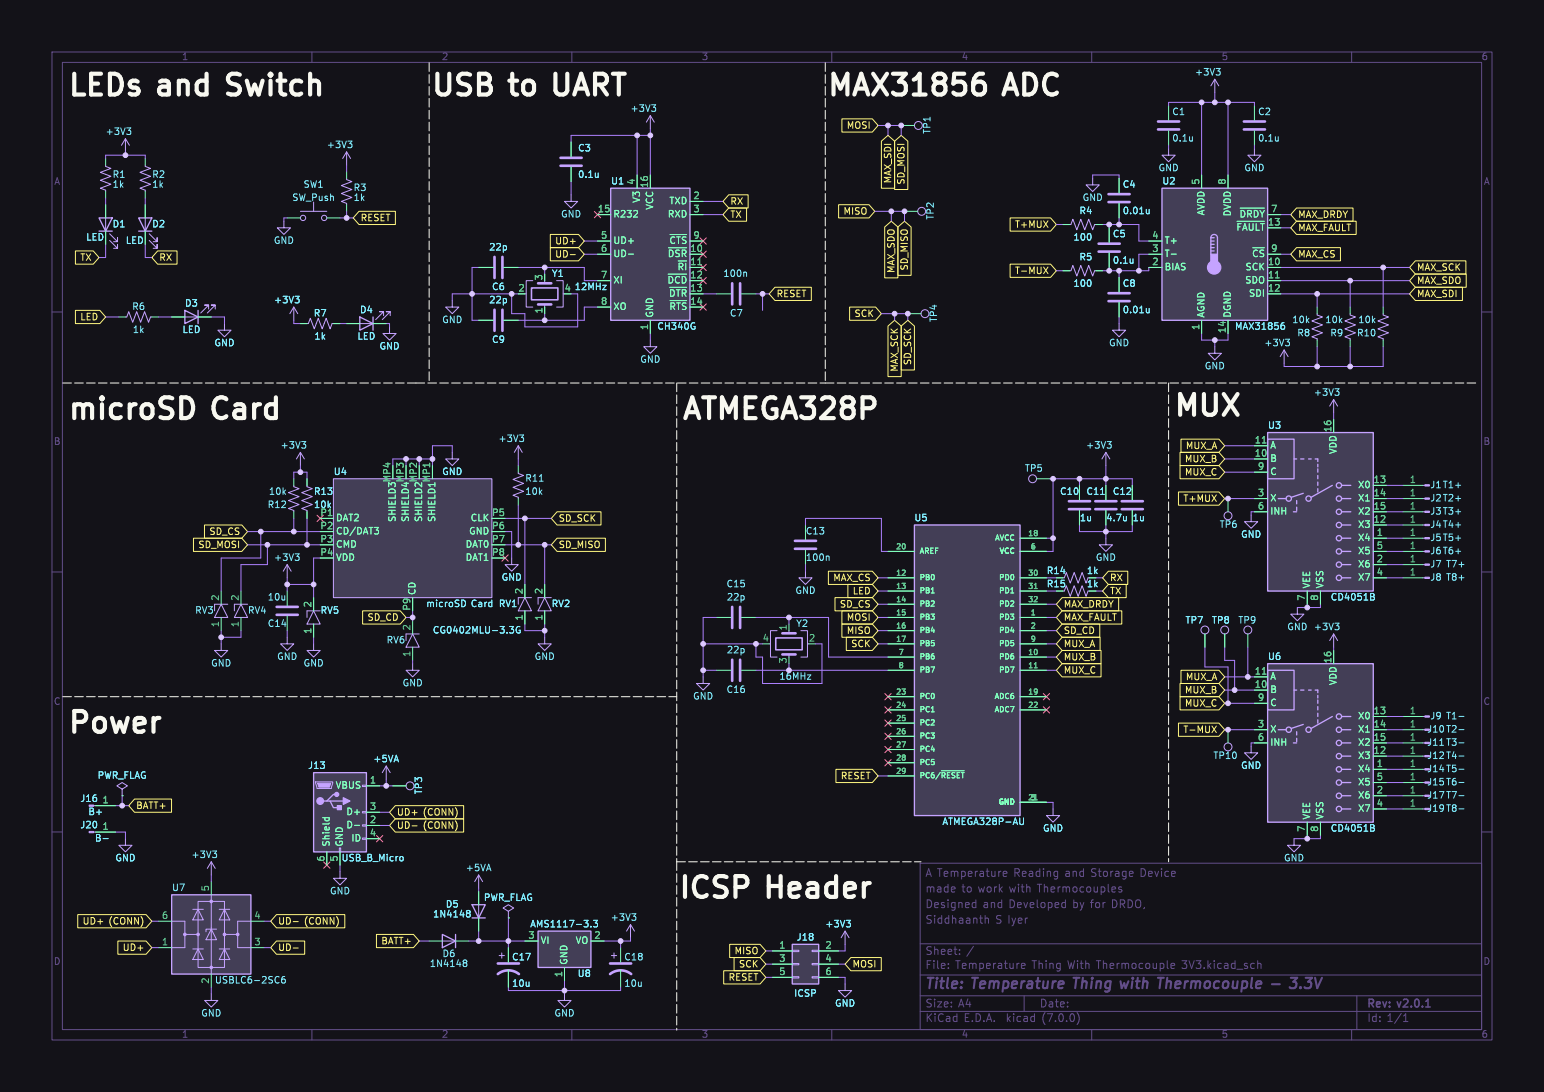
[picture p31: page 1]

4 UD+ 5 UD- 6 XI 7 XO 8 ~{CTS}9 Y1

1 ~{DSR} 10 ~{RI} 11 ~{DCD} 12 ~{DTR} 13 ~{RTS} 14 R232 15 VCC 16 TXD 2 RXD 3 V3

4 UD+ 5 UD- 6 XI 7 XO 8 ~{CTS}9 U1 CH340G

1 SCK 10 SDO 11 SDI 12 ~{FAULT} 13 DGND 14 BIAS 2 T- 3 T+ 4 AVDD

6 +5VA U4 microSD Card SHIELD1 MP1 SHIELD2 MP2 SHIELD4 MP3 SHIELD3 MP4 DAT2 P1 CD/DAT3 P2 CMD P3 VDD P4 CLK P5 GND P6 DAT0 P7 DAT1 P8 CD P9RV1

Id: 1/1 Title: Temperature Thing with Thermocouple - 3.3V

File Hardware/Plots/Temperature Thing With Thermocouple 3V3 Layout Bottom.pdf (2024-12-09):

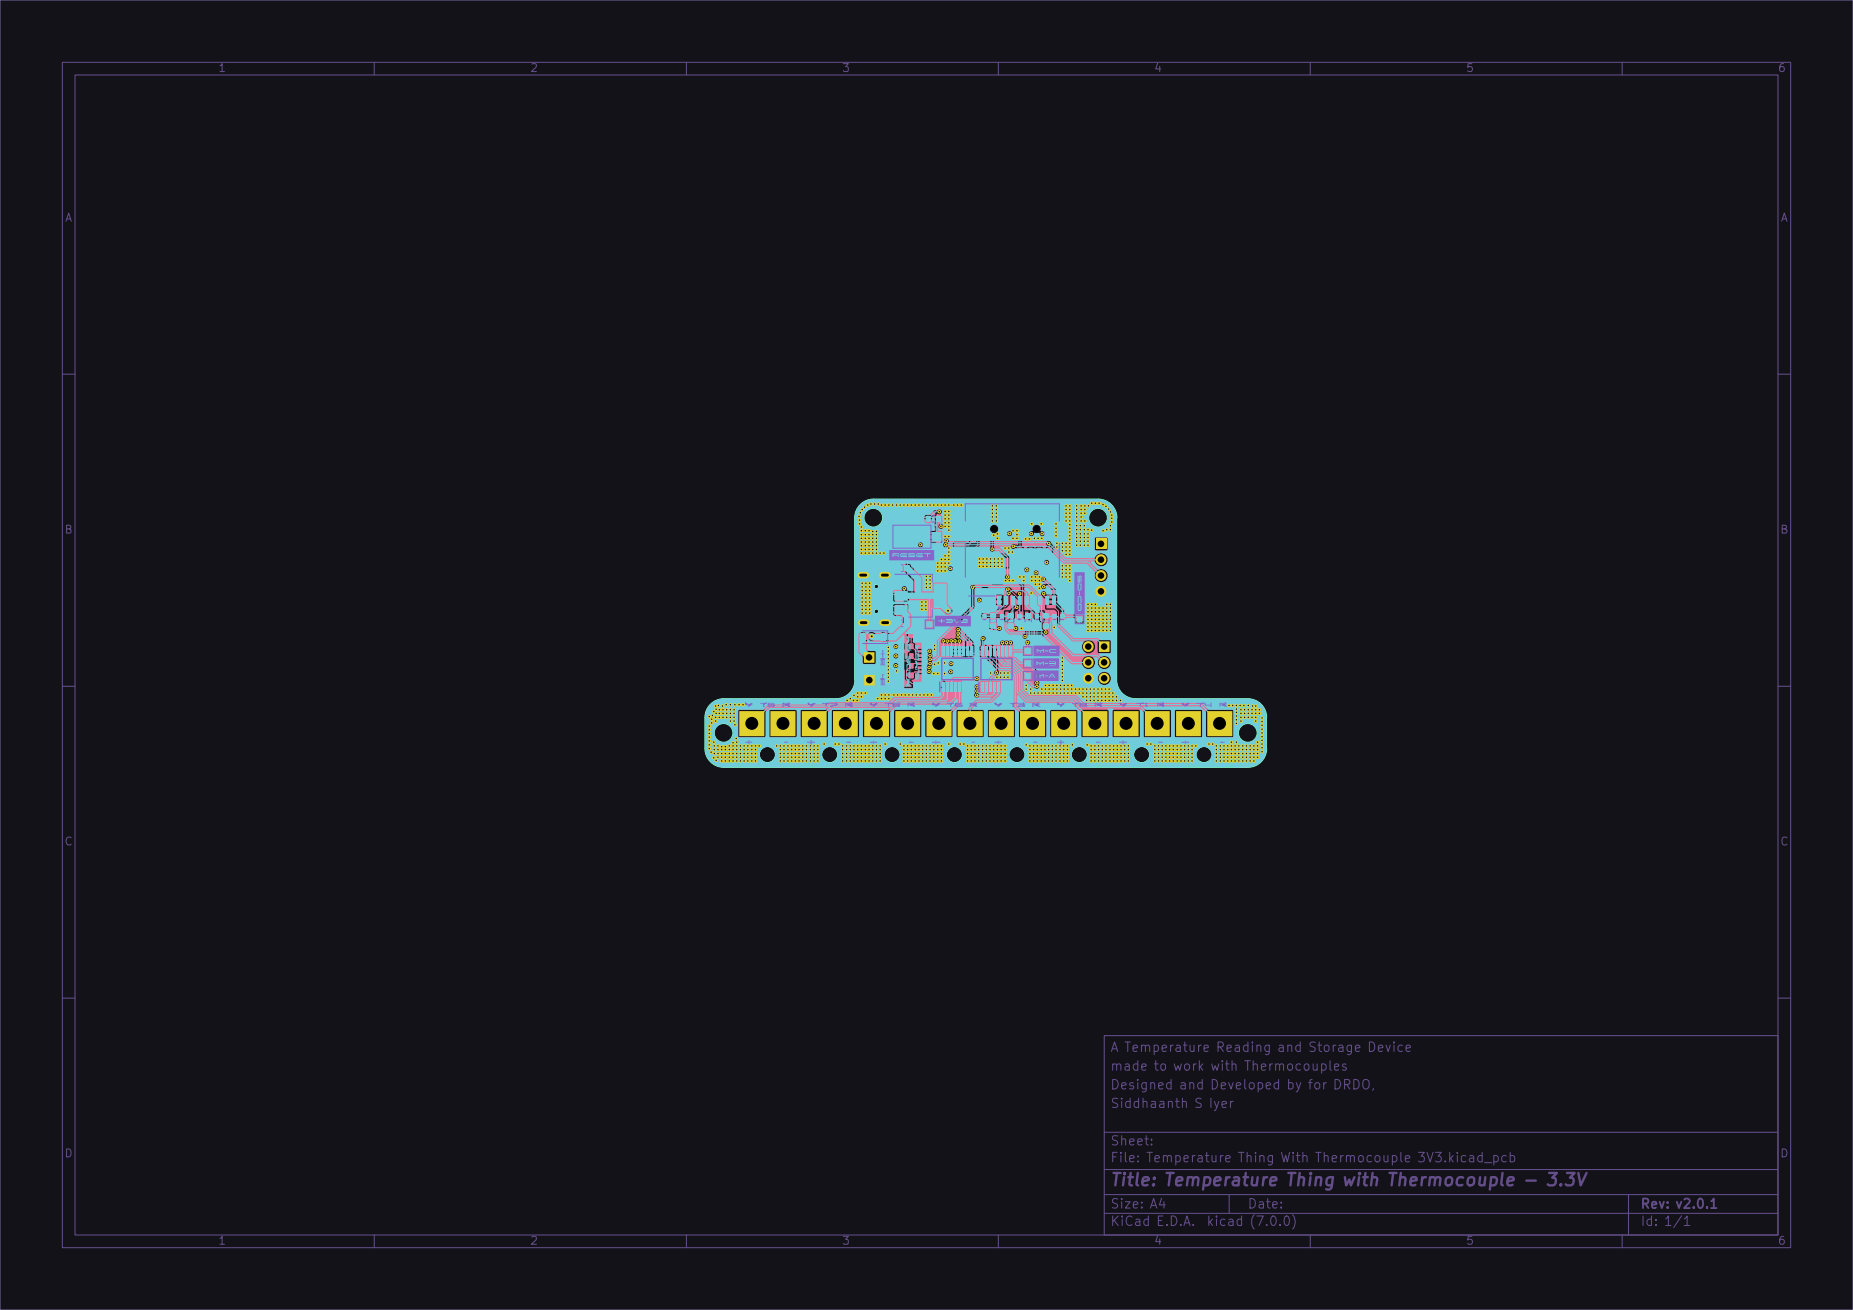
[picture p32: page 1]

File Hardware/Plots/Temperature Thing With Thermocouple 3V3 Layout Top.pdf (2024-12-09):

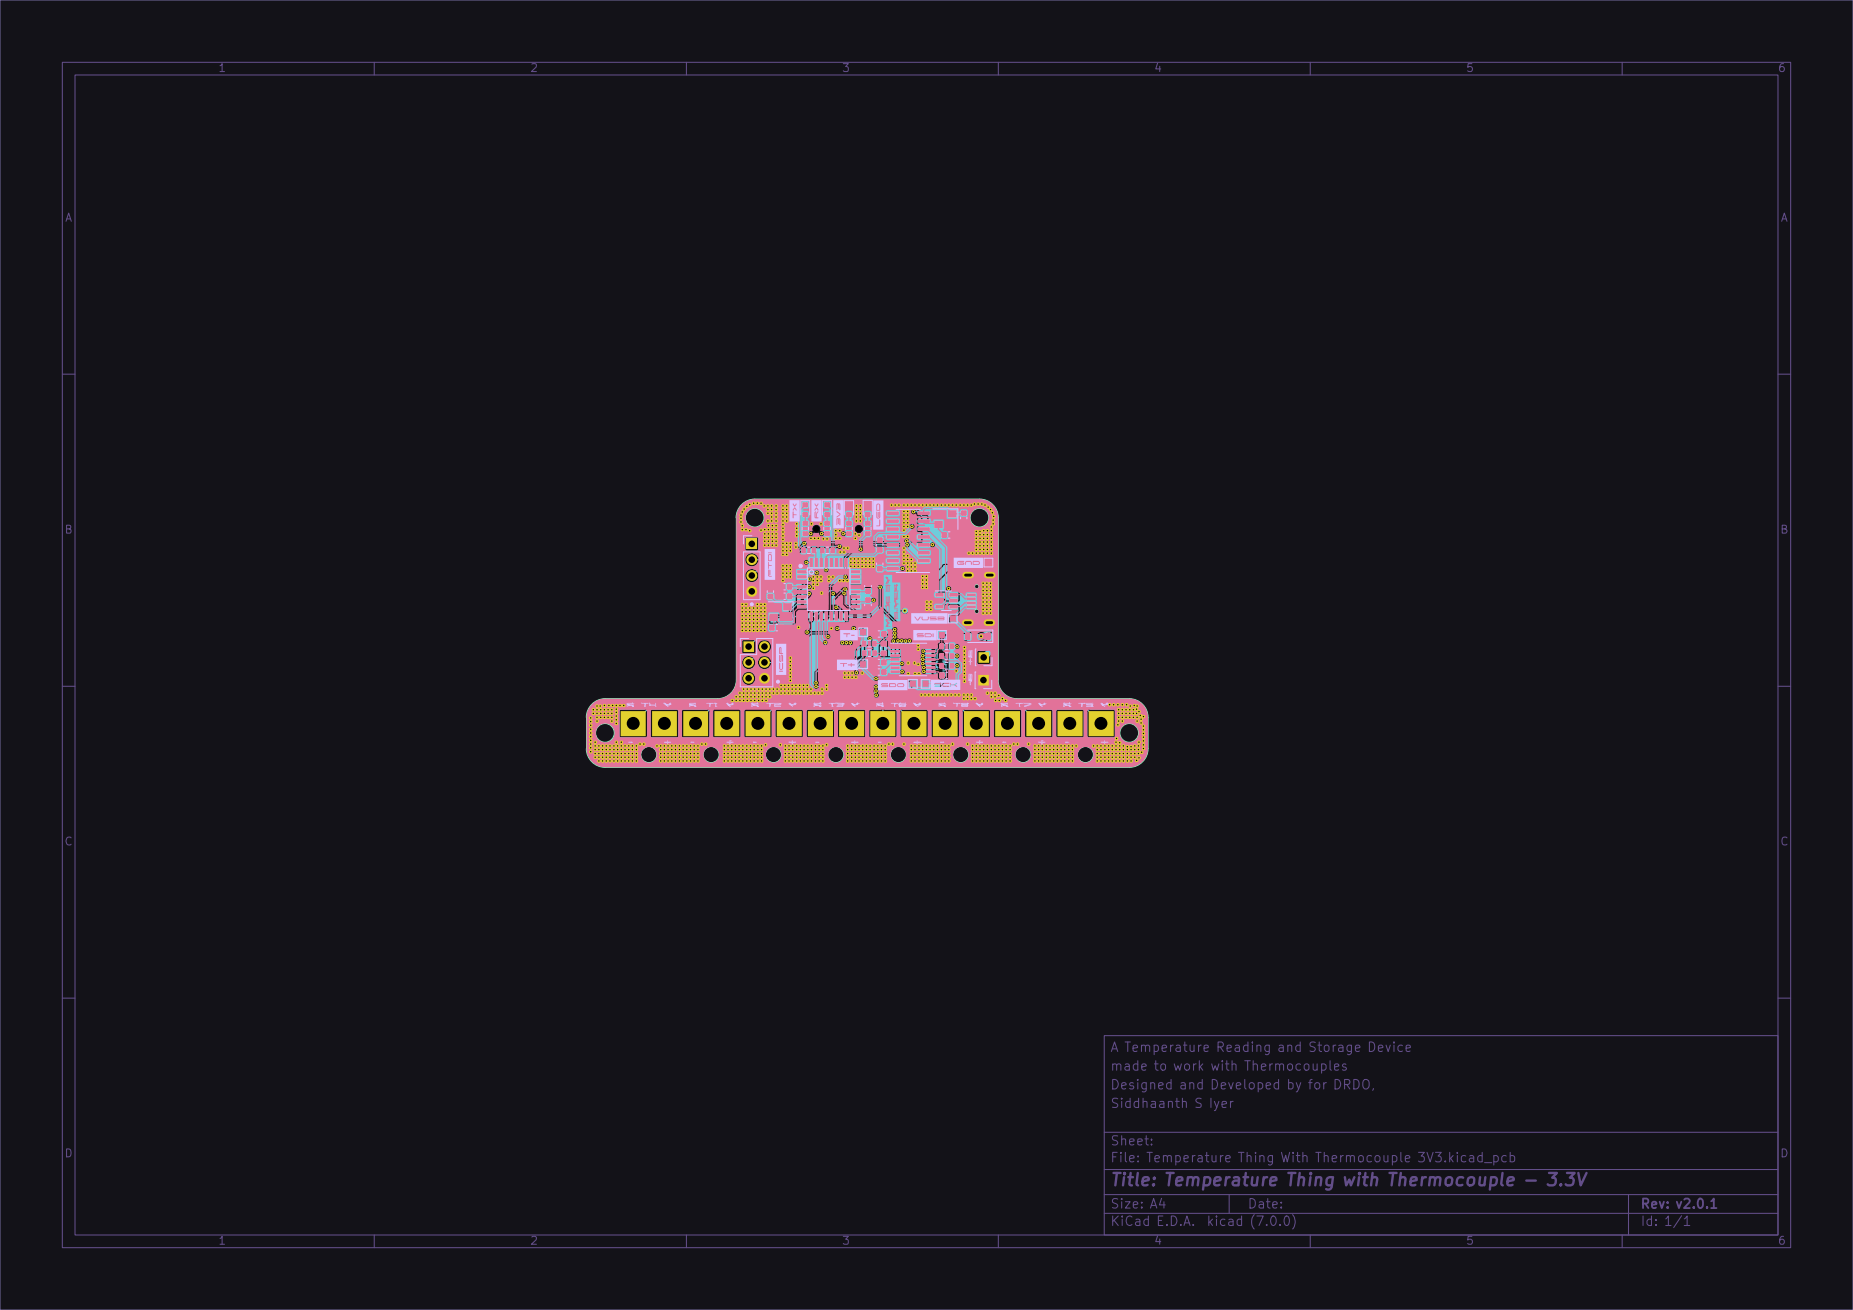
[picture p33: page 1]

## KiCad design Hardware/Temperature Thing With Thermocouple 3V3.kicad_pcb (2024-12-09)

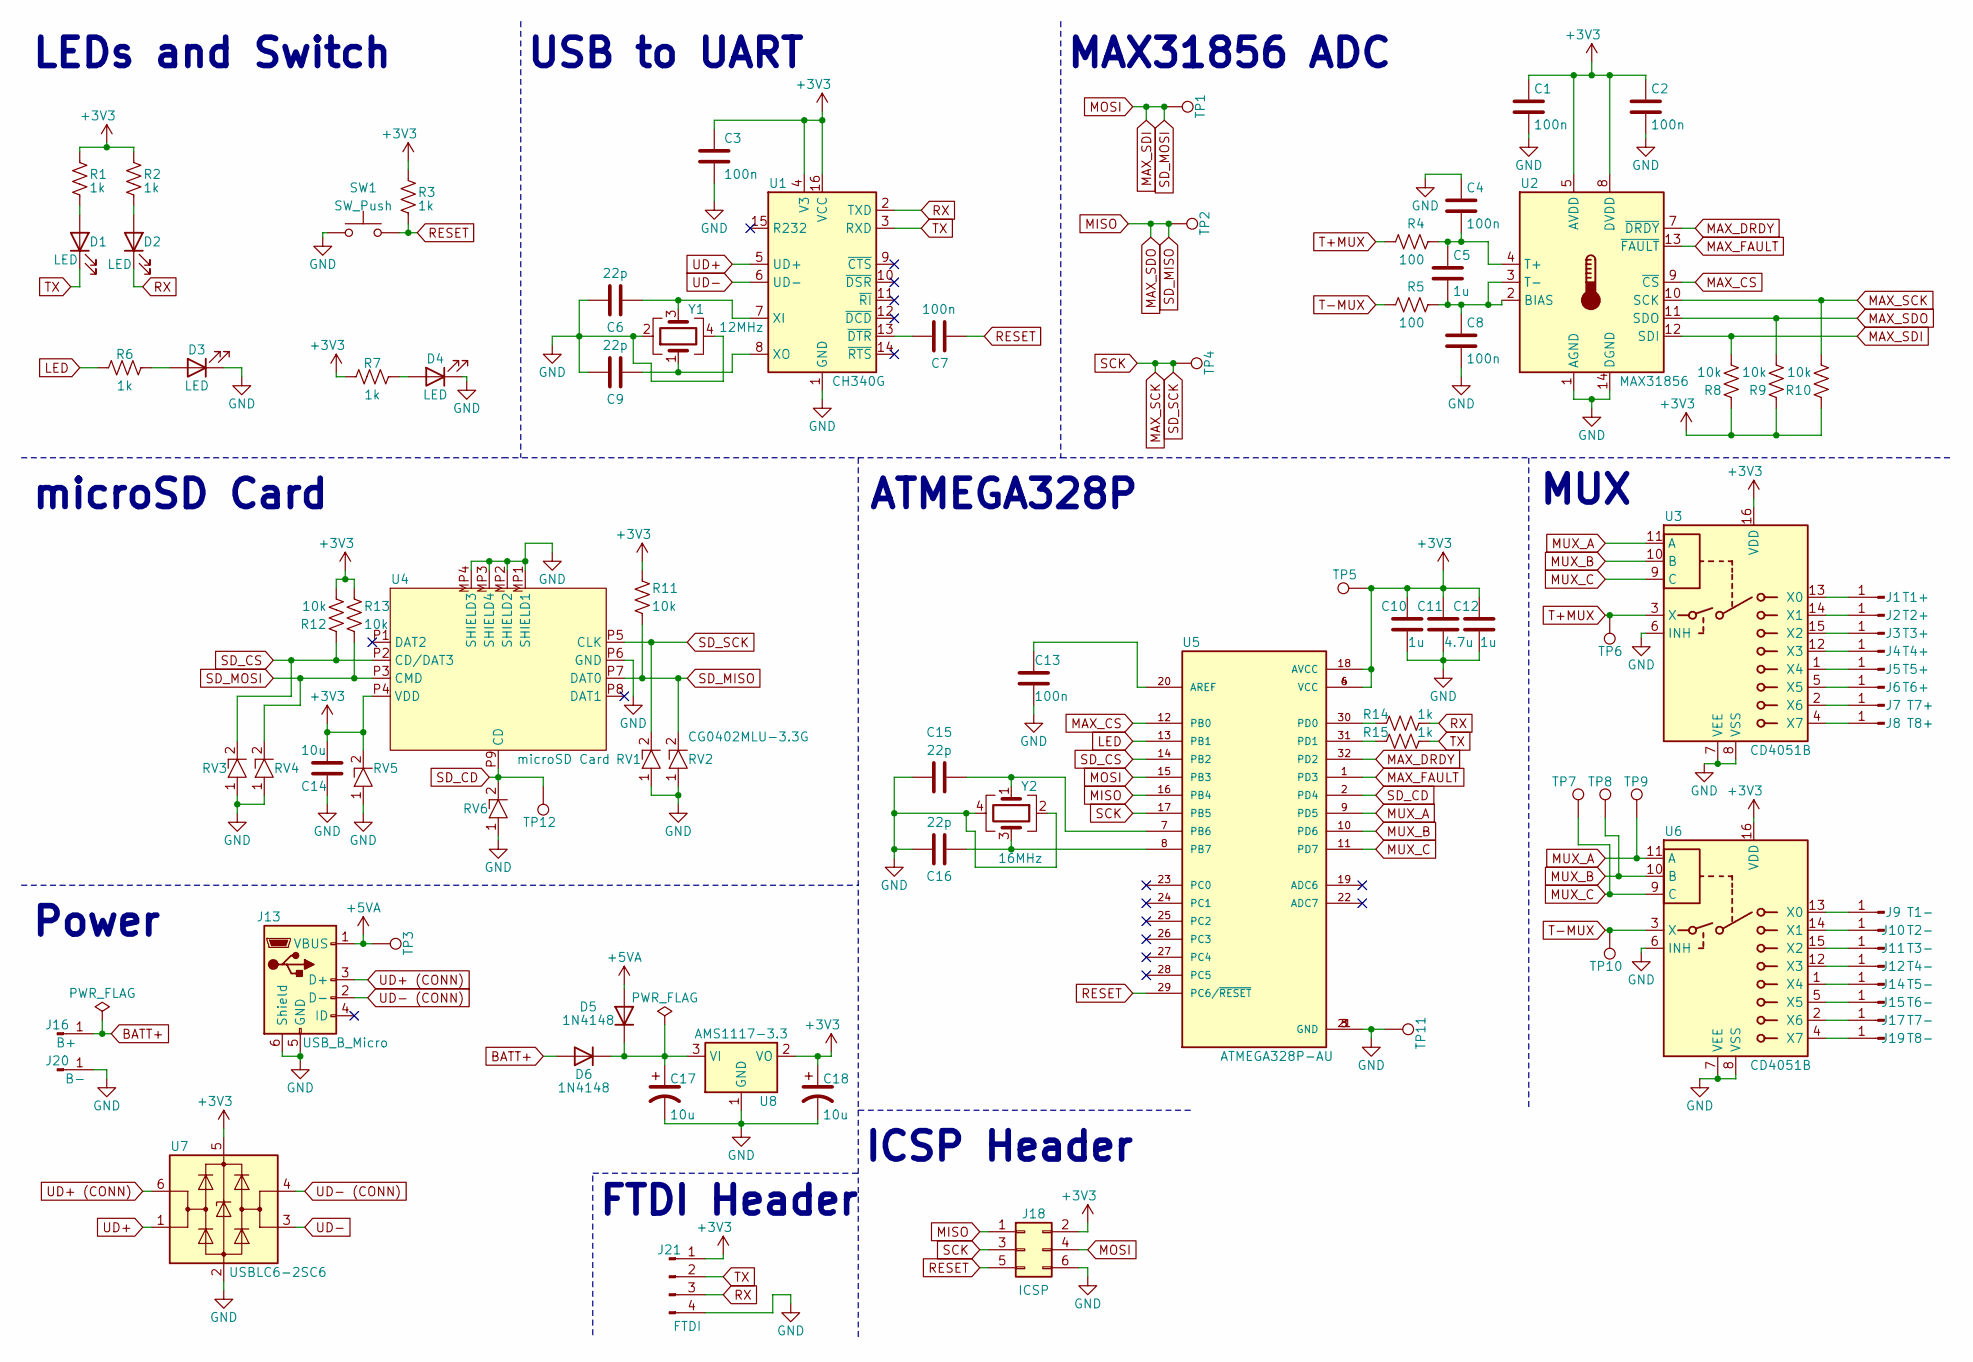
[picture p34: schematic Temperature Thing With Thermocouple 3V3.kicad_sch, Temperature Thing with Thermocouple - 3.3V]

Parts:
C1, C2, C3, C4, C7, C8, C13: 100n; C_0603_1608Metric
C5, C10, C12: 1u; C_0603_1608Metric
C6, C9, C15, C16: 22p; C_0603_1608Metric
C11: 4.7u; C_0603_1608Metric
C14, C17, C18: 10u; C_0603_1608Metric
D1, D2, D3, D4: LED; LED_0603_1608Metric
D5, D6: 1N4148; D_SOD-123
J1: T1+; M2-Plated-Hole
J2: T2+; M2-Plated-Hole
J3: T3+; M2-Plated-Hole
J4: T4+; M2-Plated-Hole
J5: T5+; M2-Plated-Hole
J6: T6+; M2-Plated-Hole
J7: T7+; M2-Plated-Hole
J8: T8+; M2-Plated-Hole
J9: T1-; M2-Plated-Hole
J10: T2-; M2-Plated-Hole
J11: T3-; M2-Plated-Hole
J12: T4-; M2-Plated-Hole
J13: USB_B_Micro; XKB-micro-USB
J14: T5-; M2-Plated-Hole
J15: T6-; M2-Plated-Hole
J16: B+; PinSocket_1x01_P2.54mm_Vertical
J17: T7-; M2-Plated-Hole
J18: ICSP; PinHeader_2x03_P2.54mm_Vertical
J19: T8-; M2-Plated-Hole
J20: B-; PinSocket_1x01_P2.54mm_Vertical
J21: FTDI; PinHeader_1x04_P2.54mm_Vertical
R1, R2, R3, R6, R7, R14, R15: 1k; R_0603_1608Metric
R4, R5: 100; R_0603_1608Metric
R8, R9, R10, R11, R12, R13: 10k; R_0603_1608Metric
RV1, RV2, RV3, RV4, RV5, RV6: CG0402MLU-3.3G; CG402MLU-3_3G; Mouser Part Number 652-CG0402MLU-3.3G
SW1: SW_Push; SW_SPST_CK_RS282G05A3
TP1, TP2, TP3, TP4, TP5, TP6, TP7, TP8, TP9, TP10, TP11, TP12: TestPoint_Pad_1.0x1.0mm
U1: CH340G; SOIC-16_3.9x9.9mm_P1.27mm
U2: MAX31856; TSSOP-14_4.4x5mm_P0.65mm
U3, U6: CD4051B; CD4051BPWR
U4: microSD Card; GCT-MICROSD-HOLDER
U5: ATMEGA328P-AU
U7: USBLC6-2SC6; SOT-23-6
U8: AMS1117-3.3; SOT-223-3_TabPin2
Y1: 12MHz; Crystal_SMD_3225-4Pin_3.2x2.5mm
Y2: 16MHz; Crystal_SMD_3225-4Pin_3.2x2.5mm

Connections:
+3V3: C1.1, C2.1, C3.2, C10.2, C11.2, C12.2, C14.1, C18.1, J18.2, J21.1, R1.1, R2.1, R3.1, R7.1, R8.1, R9.1, R10.1, R11.1, R12.2, R13.1, RV5.2, TP5.1, U1.4 (V3), U1.16 (VCC), U2.5 (AVDD), U2.8 (DVDD), U3.16 (VDD), U4.P4 (VDD), U5.4 (VCC), U5.6 (VCC), U5.18 (AVCC), U6.16 (VDD), U7.5 (VBUS), U8.2 (VO)
+5VA: D5.2 (A), J13.1 (VBUS), TP3.1
BATT+: D6.2 (A), J16.1
GND: C1.2, C2.2, C3.1, C4.1, C6.1, C8.2, C9.1, C10.1, C11.1, C12.1, C13.1, C14.2, C15.1, C16.1, C17.2, C18.2, D3.1 (K), D4.1 (K), J13.5 (GND), J13.6 (Shield), J18.6, J20.1, J21.4, RV1.1, RV2.1, RV3.1, RV4.1, RV5.1, RV6.1, SW1.1, TP11.1, U1.1 (GND), U2.1 (AGND), U2.14 (DGND), U3.6 (INH), U3.7 (VEE), U3.8 (VSS), U4.MP1 (SHIELD1), U4.MP2 (SHIELD2), U4.MP3 (SHIELD4), U4.MP4 (SHIELD3), U4.P6 (GND), U5.3 (GND), U5.5 (GND), U5.21 (GND), U6.6 (INH), U6.7 (VEE), U6.8 (VSS), U7.2 (GND), U8.1 (GND), Y1.2, Y1.4, Y2.2, Y2.4
LED: R6.2, U5.13 (PB1)
MAX_CS: U2.9 (~CS), U5.12 (PB0)
MAX_DRDY: U2.7 (~DRDY), U5.32 (PD2)
MAX_FAULT: U2.13 (~FAULT), U5.1 (PD3)
MAX_SCK: J18.3, R10.2, RV1.2, TP4.1, U2.10 (SCK), U4.P5 (CLK), U5.17 (PB5)
MAX_SDI: J18.4, R8.2, R13.2, RV4.2, TP1.1, U2.12 (SDI), U4.P3 (CMD), U5.15 (PB3)
MAX_SDO: J18.1, R9.2, R11.2, RV2.2, TP2.1, U2.11 (SDO), U4.P7 (DAT0), U5.16 (PB4)
MUX_A: TP9.1, U3.11 (A), U5.9 (PD5), U6.11 (A)
MUX_B: TP8.1, U3.10 (B), U5.10 (PD6), U6.10 (B)
MUX_C: TP7.1, U3.9 (C), U5.11 (PD7), U6.9 (C)
unnamed: C17.1, D5.1 (K), D6.1 (K), U8.3 (VI)
unnamed: D1.2 (A), R1.2
unnamed: D2.2 (A), R2.2
unnamed: D3.2 (A), R6.1
unnamed: D4.2 (A), R7.2
unnamed: J1.1, U3.13 (X0)
unnamed: J2.1, U3.14 (X1)
unnamed: J3.1, U3.15 (X2)
unnamed: J4.1, U3.12 (X3)
unnamed: J5.1, U3.1 (X4)
unnamed: J6.1, U3.5 (X5)
unnamed: J7.1, U3.2 (X6)
unnamed: J8.1, U3.4 (X7)
unnamed: J9.1, U6.13 (X0)
unnamed: J10.1, U6.14 (X1)
unnamed: J11.1, U6.15 (X2)
unnamed: J12.1, U6.12 (X3)
unnamed: J14.1, U6.1 (X4)
unnamed: J15.1, U6.5 (X5)
unnamed: J17.1, U6.2 (X6)
unnamed: J19.1, U6.4 (X7)
unnamed: C6.2, U1.7 (XI), Y1.3
unnamed: C9.2, U1.8 (XO), Y1.1
unnamed: C7.1, U1.13 (~DTR)
unnamed: C5.2, C8.1, R5.2, U2.2 (BIAS), U2.3 (T-)
unnamed: C4.2, C5.1, R4.2, U2.4 (T+)
unnamed: C13.2, U5.20 (AREF)
unnamed: C15.2, U5.7 (PB6), Y2.1
unnamed: C16.2, U5.8 (PB7), Y2.3
unnamed: R14.2, U5.30 (PD0)
unnamed: R15.2, U5.31 (PD1)
RESET: C7.2, J18.5, R3.2, SW1.2, U5.29 (PC6/~RESET)
RX: D2.1 (K), J21.3, R14.1, U1.2 (TXD)
SD_CD: RV6.2, TP12.1, U4.P9 (CD), U5.2 (PD4)
SD_CS: R12.1, RV3.2, U4.P2 (CD/DAT3), U5.14 (PB2)
T+MUX: R4.1, TP6.1, U3.3 (X)
T-MUX: R5.1, TP10.1, U6.3 (X)
TX: D1.1 (K), J21.2, R15.1, U1.3 (RXD)
UD+: U1.5 (UD+), U7.1 (I/O1)
UD+ (CONN): J13.3 (D+), U7.6 (I/O1)
UD-: U1.6 (UD-), U7.3 (I/O2)
UD- (CONN): J13.2 (D-), U7.4 (I/O2)

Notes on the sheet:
USB to UART
ATMEGA328P
LEDs and Switch
MAX31856 ADC
ICSP Header
Power
FTDI Header
MUX
microSD Card

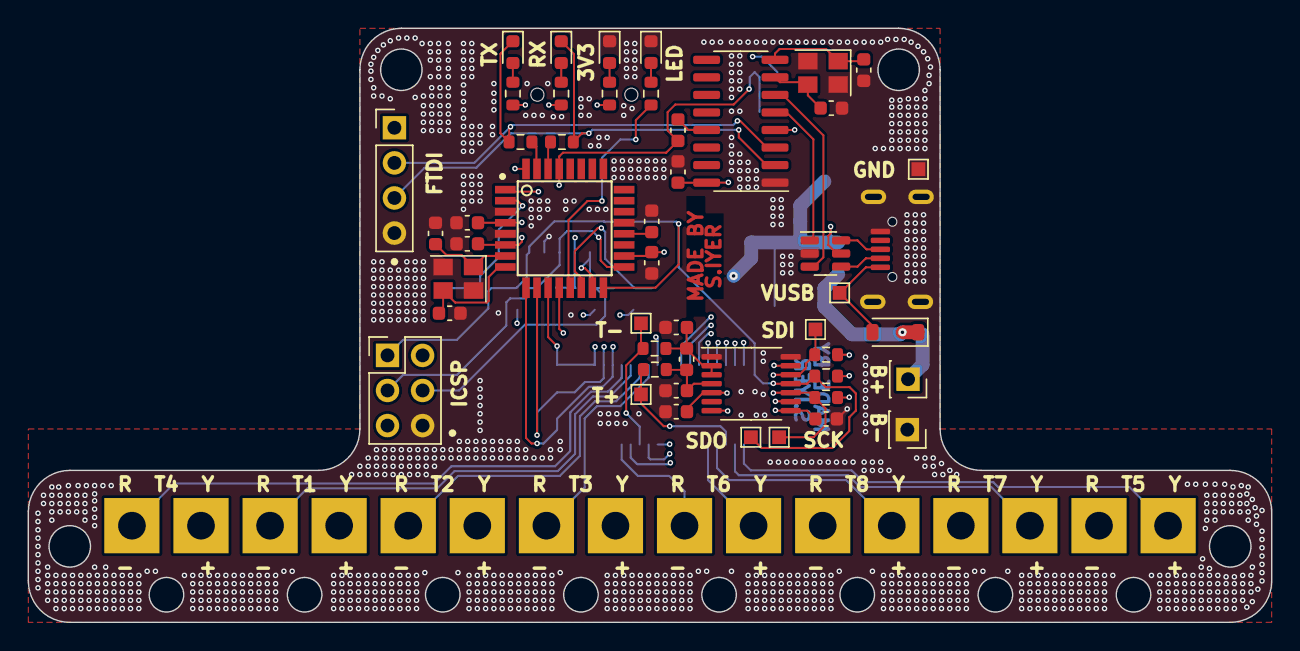
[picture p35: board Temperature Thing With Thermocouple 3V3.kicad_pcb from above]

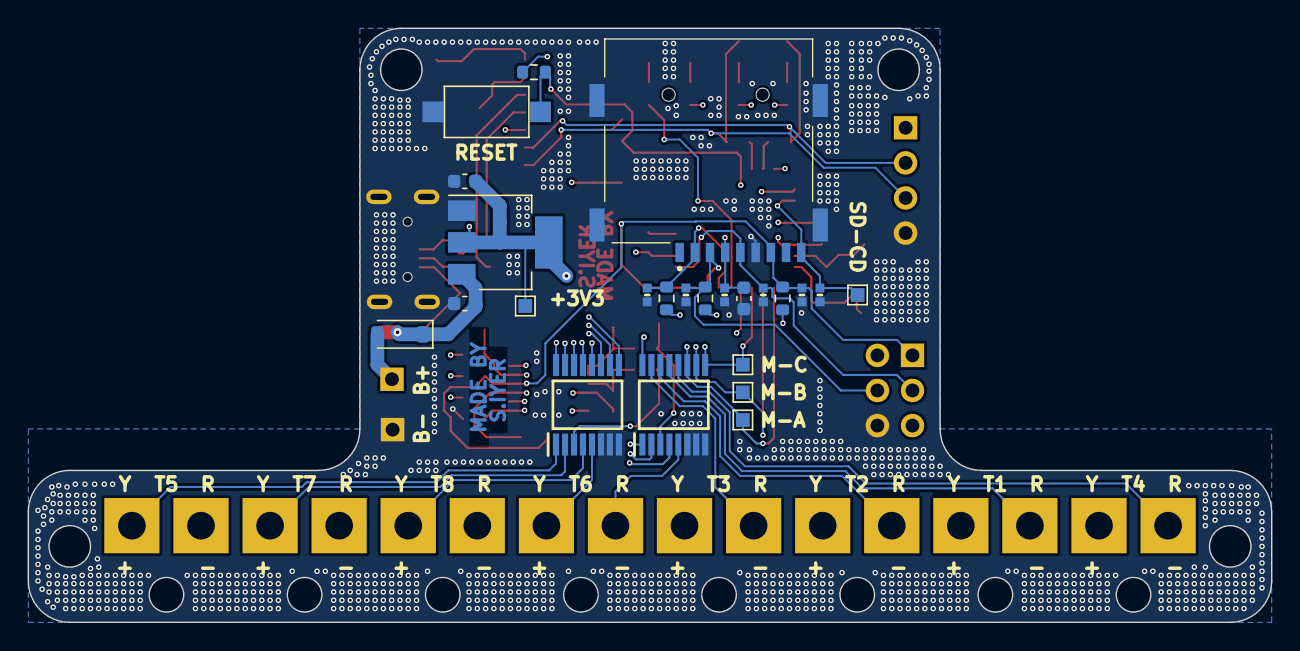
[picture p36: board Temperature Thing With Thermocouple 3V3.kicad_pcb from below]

Board: 4 copper layers, 90.0 x 43.0 mm, 89 parts (24 on the bottom side), 56 nets.

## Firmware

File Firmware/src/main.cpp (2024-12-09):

//=================================================================
//
// Copyright (c) 2024 by Siddhaanth S Iyer. All rights reserved.
//
// This material may not be reproduced, displayed, modified or
// distributed without the express prior written permission of the
// copyright holder. For permission, contact Siddhaanth S Iyer.
//
//=================================================================
//
//=======================================
// !!!!!!!!!!! Please read the README.md
// file before coming here !!!!!!!!!!!!!
//=======================================

#include <Arduino.h>
#include <MAX31856.h>
#include <SdFat.h>

#define LED_PIN 9
#define MUX_PIN_A 5
#define MUX_PIN_B 6	
#define MUX_PIN_C 7
#define MAX_CS 8
#define SD_CS 10
#define SD_CD 4
#define MAX_FAULT 3
#define MAX_DATA_READY 2

#define SWITCHING_DELAY_MS 220
#define NUM_THERMOCOUPLES 8

const int BOARD_PINS[] = {LED_PIN, MAX_CS, SD_CS, SD_CD, MAX_FAULT, MAX_DATA_READY};
const int BOARD_PIN_DIR[] = {OUTPUT, OUTPUT, OUTPUT, INPUT, INPUT, INPUT};
const int MUX_PINS[] = {MUX_PIN_A, MUX_PIN_B, MUX_PIN_C};

double ColdJunctionTemp;
double ThermocoupleTemp[NUM_THERMOCOUPLES];
unsigned int timeStamp;

MAX31856 MAX;
SdFat SD;
File dataFile;

/**
 * \brief Function to indicate any failure
 * \param None
 * \return None
 */
void showFailure()
{
	digitalWrite(LED_PIN, HIGH);
	delay(250);
	digitalWrite(LED_PIN, LOW);
	delay(250);
}

/**
 * \brief Function to indicate successful initialisation
 * \param None
 * \return None
 */
void showSuccess()
{
	digitalWrite(LED_PIN, HIGH);
	delay(1000);
	digitalWrite(LED_PIN, LOW);
	delay(1000);
}

/**
 * \brief Function to select a specific MUX pin
 * \param Pin_Number The pin to be selected (0-7)
 * \return None
 */
void selectPin(int Pin_Number)
{
	for (int Pin = 0; Pin < 3; Pin++)
		digitalWrite(MUX_PINS[Pin], (Pin_Number & (1 << Pin)) != 0);
}

/**
 * \brief Function to read a single thermocouple
 * \param Thermocouple_Number The pin number of the thermocouple to be read (1-8)
 * \return None
 */
void readSingleThermocouple(int Thermocouple_Number)
{
	selectPin(Thermocouple_Number - 1);
	delay(SWITCHING_DELAY_MS);
	ThermocoupleTemp[Thermocouple_Number - 1] = MAX.readThermocoupleTemperature();
}

/**
 * \brief Function to cycle through all thermocouples
 * \param None
 * \return None
 */
void cycleThroughThermocouples()
{
	digitalWrite(LED_PIN, HIGH);
	for (int i = 1; i <= NUM_THERMOCOUPLES; i++)
		readSingleThermocouple(i);

	ColdJunctionTemp = MAX.readCJTemperature();
	Serial.print(timeStamp);
	Serial.print(",");
	for (int i = 0; i < NUM_THERMOCOUPLES; i++)
	{
		Serial.print(ThermocoupleTemp[i]);
		Serial.print(",");
	}
	Serial.println(ColdJunctionTemp);
	digitalWrite(LED_PIN, LOW);
}

/// \brief Setup Function
void setup()
{
	for (int i = 0; i < int(sizeof(BOARD_PINS) / sizeof(int)); i++)
		pinMode(BOARD_PINS[i], BOARD_PIN_DIR[i]);
	for (int i = 0; i < 3; i++)
		pinMode(MUX_PINS[i], OUTPUT);
	delayMicroseconds(10);
	Serial.begin(9600);
	digitalWrite(MAX_CS, HIGH);
	digitalWrite(SD_CS, HIGH);
	SD.begin(SD_CS);
	SD.remove("data.txt");
	SD.end();
}

/// \brief Loop Function
void loop()
{
	delay(1);
	digitalWrite(SD_CS, HIGH);
	MAX.begin(MAX_CS);
	timeStamp = millis() / 1000;
	cycleThroughThermocouples();
	delay(1);
	digitalWrite(MAX_CS, HIGH);
	SD.begin(SD_CS);
	dataFile = SD.open("data.txt", FILE_WRITE);
	if (dataFile)
	{
		dataFile.print(timeStamp);
		dataFile.print(",");
		for (int i = 0; i < NUM_THERMOCOUPLES; i++)
		{
			dataFile.print(ThermocoupleTemp[i]);
			dataFile.print(",");
		}
		dataFile.println(ColdJunctionTemp);
		dataFile.close();
	}
	SD.end();
}

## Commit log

2024-04-07 Create troubleshooting-device
    GUI-component for troubleshooting
2024-07-16 Bump pillow from 9.4.9 to 10.3.0 in /SDA-troubleshooting-device
    Bumps [pillow](https://github.com/python-pillow/Pillow) from 9.4.9 to 10.3.0.
    - [Release notes](https://github.com/python-pillow/Pillow/releases)
    - [Changelog](https://github.com/python-pillow/Pillow/blob/main/CHANGES.rst)
    - [Commits](https://github.com/python-pillow/Pillow/commits/10.3.0)
    ---
    updated-dependencies:
    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
